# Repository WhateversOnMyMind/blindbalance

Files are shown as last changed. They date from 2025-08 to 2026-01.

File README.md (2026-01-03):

<<<<<<< HEAD
# Objective
Build a device that uses 2 MPU6050 sensors on each elbow to track arm swings (count and distance) to give feedback to user on how to improve arm swing balance and ultimately better posture
=======
>>>>>>> 9a92b26fbc7dfd73c1ad28d76f8ad0d9f775afb2
# Introduction
Hi, this is my project where I try to make a device that tracks your movement with information from a mix of accelerometers and gyroscopes (linear acceleration and radial acceleration) to track arm swings. 

So, why did I start this project?

Let's start from the beginning.
I do this activity at Namsan Mountain where I run with visually impaired runners with a running tether. 

running tether

It keeps the visually impaired runner parallel to the volunteer (me) and lets me pull the runner in case of any obstacles / people. 
Most tethers (all tethers I've seen) are inelastic, thus the blind runners naturally doesn't swing the arm that's tied.
It would be fine if the blind runners switched their tether arm every run, but most runners just make it a habit of using the tether on the same arm always.
Keep running with this habit can become a cause for unbalanced posture.
I didn't notice it in my 2 years of running with visually impaired runners.
But my mom did when she took a look at a group photo that was taken at the event.
Thinking about it, I found out that the blind have a higher COG (center of gravity) velocity ([https://doi.org/10.1002/brb3.1436](https://doi.org/10.1002/brb3.1436)), and thus were more susceptible to bad posture.
This started my journey to find a device to give feedback to blind runners to promote balanced posture through equalizing left and right arm swings (both count and distance).

# 8/4

 - Arduino Basics

→ Learned Digital Inputs
```
    // constants won't change. They're used here to set pin numbers:
    const int buttonPin = 2;     // the number of the pushbutton pin
    const int ledPin =  13;      // the number of the LED pin
    
    // variables will change:
    int buttonState = 0;         // variable for reading the pushbutton status
    
    void setup() {
      // initialize the LED pin as an output:
      pinMode(ledPin, OUTPUT);
      // initialize the pushbutton pin as an input:
      pinMode(buttonPin, INPUT);
    }
    
    void loop() {
      // read the state of the pushbutton value:
      buttonState = digitalRead(buttonPin);
    
      // check if the pushbutton is pressed. If it is, the buttonState is HIGH:
      if (buttonState == HIGH) {
        // turn LED on:
        digitalWrite(ledPin, HIGH);
      } else {
        // turn LED off:
        digitalWrite(ledPin, LOW);
      }
    }
```
→ Learned Analog Inputs and Libraries (And also some debugging & syntax)

Debugging
```
void setup() {
  // initialize serial communication at 9600 bits per second:
  Serial.begin(9600);
}

// the loop routine runs over and over again forever:
void loop() {
  // read the input on analog pin 0:
  int sensorValue = analogRead(A0);
  // print out the value you read:
  Serial.println(sensorValue);
  delay(1);        // delay in between reads for stability
}
```
Analog Inputs + rgb lights
```
#include <Adafruit_NeoPixel.h>
#ifdef __AVR__
 #include <avr/power.h> // Required for 16 MHz Adafruit Trinket
#endif
#define PIN 13
#define NUMPIXELS 3
Adafruit_NeoPixel pixels(NUMPIXELS, PIN, NEO_GRB + NEO_KHZ800);
#define DELAYVAL 500
void color(uint16_t pixelIndex, uint8_t red, uint8_t green, uint8_t blue) {
  pixels.setPixelColor(pixelIndex, pixels.Color(red, green, blue));
}
void setup() {
#if defined(__AVR_ATtiny85__) && (F_CPU == 16000000)
  clock_prescale_set(clock_div_1);
#endif
  pixels.begin();
 pinMode(A0, INPUT);
}

void loop() {
  int raw = analogRead(A0);
  int scrollValue = map(raw, 0, 1023, 0, 255);
  color(0, scrollValue, 0, 0);
  color(1, 0, scrollValue, 0);
  color(2, 0, 0, scrollValue);
  pixels.show();
}
```

 - Sketchup Pro Basics
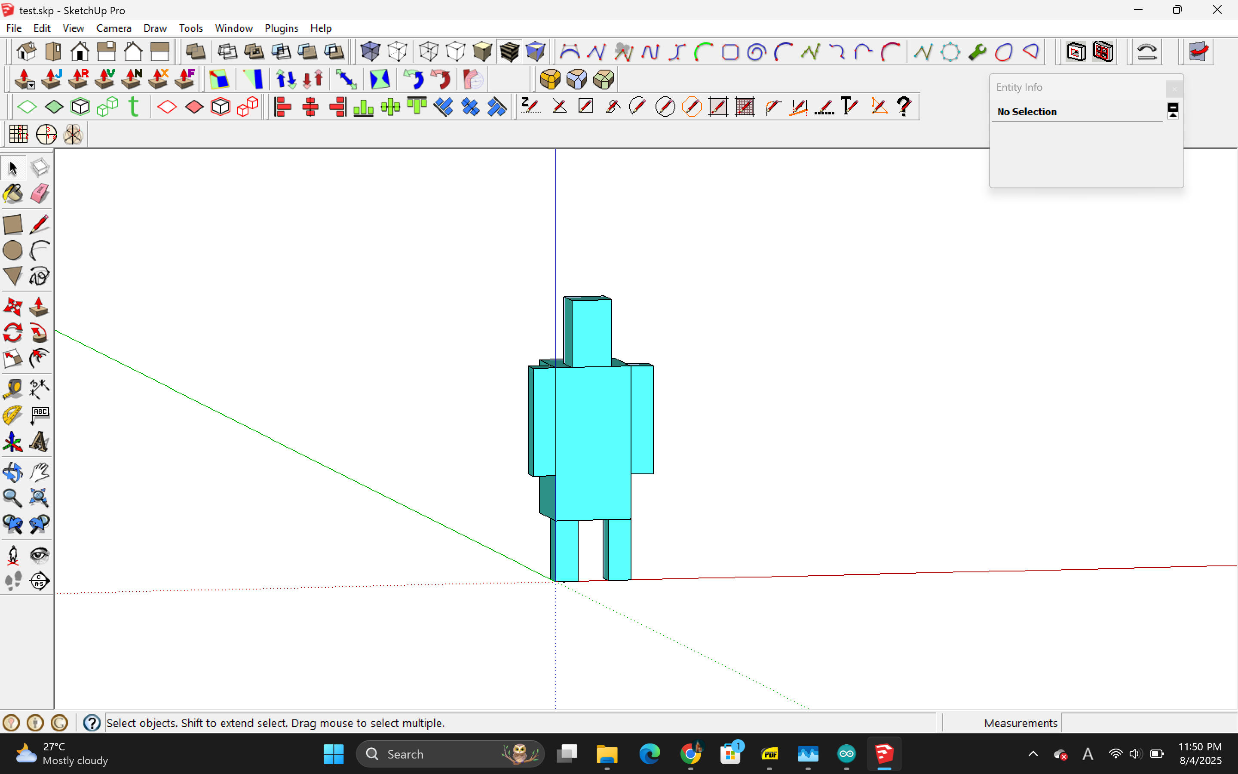
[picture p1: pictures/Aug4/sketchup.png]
Just basic stuff. Can 3-dimensionally print it!!
 

# 8/5
- Arduino coding

Simple double integration model to track motion (print distance every 200ms)
```
#include <Adafruit_MPU6050.h>
#include <Adafruit_Sensor.h>
#include <Wire.h>

Adafruit_MPU6050 mpu;

// ---- calibration storage ----
float axBias = 0, ayBias = 0, azBias = 0;

// ---- state variables ----
float vx = 0, vy = 0, vz = 0;   // velocity (m/s)
float px = 0, py = 0, pz = 0;   // position (m)
unsigned long lastMicros = 0;

void setup() {
  Serial.begin(115200);
  Wire.begin(21, 22);           // LOLIN-D32 default I²C
  if (!mpu.begin()) {
    Serial.println("MPU6050 not found!"); while (1) delay(10);
  }
  mpu.setAccelerometerRange(MPU6050_RANGE_8_G);
  mpu.setFilterBandwidth(MPU6050_BAND_21_HZ);

  Serial.println("\n*** Keep the board STILL for 2 s — calibrating… ***");
  const int N = 400;            // 2 s at 200 Hz
  sensors_event_t a, g, t;
  for (int i = 0; i < N; ++i) {
    mpu.getEvent(&a, &g, &t);
    axBias += a.acceleration.x;
    ayBias += a.acceleration.y;
    azBias += a.acceleration.z - 9.80665;  // remove gravity on Z
    delay(5);
  }
  axBias /= N; ayBias /= N; azBias /= N;
  Serial.println("Calibration done.\n");

  lastMicros = micros();
}

void loop() {
  // -------- time step --------
  unsigned long now = micros();
  float dt = (now - lastMicros) * 1e-6;   // s
  lastMicros = now;

  // -------- read accel --------
  sensors_event_t a, g, t;
  mpu.getEvent(&a, &g, &t);
  float ax = a.acceleration.x - axBias;
  float ay = a.acceleration.y - ayBias;
  float az = a.acceleration.z - azBias;

  // -------- integrate --------
  vx += ax * dt;
  vy += ay * dt;
  vz += az * dt;

  px += vx * dt;
  py += vy * dt;
  pz += vz * dt;

  // -------- print every 200 ms --------
  static unsigned long lastPrint = 0;
  if (millis() - lastPrint >= 200) {
    lastPrint = millis();
    Serial.print("ΔPos X: "); Serial.print(px, 4);
    Serial.print("  Y: ");    Serial.print(py, 4);
    Serial.print("  Z: ");    Serial.print(pz, 4);
    Serial.println("  (m)");
  }
}
```
This time a different approach:
Counts arm swing count by using IMU sensors (MPU6050)
Also has an automatic 2-second gyro sensor calibration period
```
#include <Adafruit_MPU6050.h>
#include <Adafruit_Sensor.h>
#include <Wire.h>

#define SDA_PIN          21
#define SCL_PIN          22
#define SAMPLE_RATE_HZ   250          // loop target ≈ 4 ms
#define GYRO_THRESH      1.2f         // rad/s   (swing detected when |ωz| crosses this)
#define RADIUS_DEFAULT   0.30f        // m       (fore-arm length – user adjustable)
#define CALIB_TIME_MS    2000         // how long to average gyro bias

Adafruit_MPU6050 mpu;

/* ------------------------ runtime state ------------------------ */
float gzBias = 0.0f;                  // gyro Z bias (rad/s)
float radius = RADIUS_DEFAULT;        // swing radius (m)

float angleZ = 0.0f;                  // integrated θ (rad) – continuous
bool  inSwing = false;                // currently inside a swing?
int   dir      = 0;                   // +1 forward, -1 backward
float swingStartAngle = 0.0f;         // θ at swing start
uint32_t swingCount = 0;

uint64_t lastMicros = 0;

/* ----------------------------- helpers ----------------------------- */
void calibrateGyro()
{
  Serial.println(F("\n*** Keep sensor STILL – calibrating gyro (2 s)… ***"));
  delay(500);
  const uint32_t t0 = millis();
  uint32_t samples = 0;
  float sum = 0.0f;
  sensors_event_t a, g, t;
  while (millis() - t0 < CALIB_TIME_MS) {
    mpu.getEvent(&a, &g, &t);
    sum += g.gyro.z;
    ++samples;
    delay(4);
  }
  gzBias = sum / samples;
  Serial.print(F("Gyro Z bias = "));
  Serial.print(gzBias, 6);
  Serial.println(F(" rad/s"));
  angleZ = 0; inSwing = false; dir = 0;
}

void processSerial()
{
  if (!Serial.available()) return;
  char c = Serial.read();
  if (c == 'r')            calibrateGyro();               // recalibrate bias
  else if (c == 'd') {                                   // set new radius
    float newR = Serial.parseFloat();
    if (newR > 0.05 && newR < 1.0) {
      radius = newR;
      Serial.print(F("Swing radius set to "));
      Serial.print(radius * 100.0f, 1);
      Serial.println(F(" cm"));
    }
  }
}

/* ----------------------------- setup ----------------------------- */
void setup()
{
  Serial.begin(115200);
  Wire.begin(SDA_PIN, SCL_PIN);
  if (!mpu.begin()) { Serial.println(F("MPU6050 not found!")); while (1) delay(10); }

  mpu.setGyroRange(MPU6050_RANGE_500_DEG);      //  ±500 °/s  ≈ 8.73 rad/s
  mpu.setFilterBandwidth(MPU6050_BAND_21_HZ);   //  basic LPF

  calibrateGyro();
  lastMicros = micros();

  Serial.println(F("\nSend ‘r’ to recalibrate bias, ‘d <value>’ to set radius in metres\n"));
}

/* ----------------------------- loop ----------------------------- */
void loop()
{
  /* ----- timing ----- */
  uint64_t now = micros();
  float dt = (now - lastMicros) * 1e-6f;
  lastMicros = now;

  /* ----- read IMU ----- */
  sensors_event_t a, g, t;
  mpu.getEvent(&a, &g, &t);
  float wz = g.gyro.z - gzBias;        // rad/s  (Z-axis angular velocity)

  /* ----- integrate θz ----- */
  angleZ += wz * dt;                   // rad (unbounded)

  /* ----- swing detection FSM ----- */
  if (!inSwing) {
    /* detect start: |ω| crosses threshold */
    if (fabsf(wz) > GYRO_THRESH) {
      inSwing           = true;
      dir               = (wz > 0) ? 1 : -1;
      swingStartAngle   = angleZ;
    }
  }
  else {
    /* detect end: sign reversal AND exceeded threshold in opposite dir */
    if ((dir ==  1 && wz < -GYRO_THRESH) ||
        (dir == -1 && wz >  GYRO_THRESH)) {
      float swingEndAngle = angleZ;
      float deltaTheta    = swingEndAngle - swingStartAngle;   // rad (can be ±)
      float arcLen        = fabsf(deltaTheta) * radius;        // m

      ++swingCount;
      Serial.print("Swing #");  Serial.print(swingCount);
      Serial.print(" │ Angle: "); Serial.print(fabsf(deltaTheta) * 57.29578f, 1); Serial.print(" deg");
      Serial.print(" │ Length: "); Serial.print(arcLen * 100.0f, 1); Serial.println(" cm");

      /* ready for next swing */
      inSwing = false;
    }
  }

  processSerial();
  delayMicroseconds(1000000 / SAMPLE_RATE_HZ - 200);   // crude pacing
}
```
Tried some other concepts like counting when angular acceleration turned negative or when it reached zero, but those attempts didn't work as well since human movements are a bit unpredictable → counted mid-swing

Eventually stuck with the above code although with more polishing and adjustments
I didn't really why it still gave me false counts (swings), turns out I had to use the y-axis instead of the z-axis.
Also, I separated the swing thresholds for forward and backward motion and made both lower than the original thresholds since, well, you don't really drastically swing your arms when you're jogging right?
```
#include <Adafruit_MPU6050.h>
#include <Adafruit_Sensor.h>
#include <Wire.h>

/* ── pins ── */
#define SDA_PIN              21
#define SCL_PIN              22

/* ── sampling & calibration ── */
#define SAMPLE_RATE_HZ       250        // ≈4 ms loop
#define CALIB_TIME_MS        2000       // 2 s gyro-bias average

/* ── swing thresholds (provided) ── */
#define GYRO_THRESH_FWD      0.4f       // rad/s  forward swing must exceed
#define GYRO_THRESH_BACK     0.2f       // rad/s  backward swing must exceed
#define MIN_DELTA_THETA      0.12f      // rad ≈ 7°  ignore tiny jitters

/* ── geometry ── */
#define RADIUS_DEFAULT       0.30f      // m  elbow→wrist

/* ── globals ── */
Adafruit_MPU6050 mpu;

float gyBias  = 0.0f;                  // Y-axis bias
float radius  = RADIUS_DEFAULT;

bool  inSwing = false;
int   dir     = 0;                     // +1 = forward, –1 = backward
float angle   = 0.0f;                  // integrated θ about Y (rad)
float startAngle = 0.0f;
uint32_t swingCount = 0;

uint64_t lastMicros = 0;

/* ─────────── helpers ─────────── */
void printSwing(float endAngle)
{
  float dTheta = endAngle - startAngle;
  if (fabsf(dTheta) < MIN_DELTA_THETA) { inSwing = false; return; }  // too small

  ++swingCount;
  float arcLen = fabsf(dTheta) * radius;            // m

  Serial.print(F("Swing #"));  Serial.print(swingCount);
  Serial.print(F(" │ Angle: "));  Serial.print(fabsf(dTheta) * 57.29578f, 1);
  Serial.print(F(" ° │ Length: ")); Serial.print(arcLen * 100.0f, 1);
  Serial.println(F(" cm"));
  inSwing = false;
}

void calibrateGyro()
{
  Serial.println(F("\n*** Keep sensor STILL – calibrating (2 s)… ***"));
  delay(400);
  uint32_t t0 = millis();  float sum = 0;  uint32_t n = 0;
  sensors_event_t a, g, t;
  while (millis() - t0 < CALIB_TIME_MS) {
    mpu.getEvent(&a, &g, &t);
    sum += g.gyro.y;  ++n;  delay(4);
  }
  gyBias = sum / n;

  swingCount = 0; angle = 0; inSwing = false; dir = 0;
  Serial.print(F("Gyro-Y bias = ")); Serial.print(gyBias, 6); Serial.println(F(" rad/s"));
}

void serialMenu()
{
  if (!Serial.available()) return;
  char c = Serial.read();
  if (c == 'r') calibrateGyro();
  else if (c == 'd') {
    float r = Serial.parseFloat();
    if (r > 0.05 && r < 1.0) {
      radius = r;
      Serial.print(F("Radius set to ")); Serial.print(radius * 100.0f, 1);
      Serial.println(F(" cm"));
    }
  }
}

/* ─────────── setup ─────────── */
void setup()
{
  Serial.begin(115200);
  Wire.begin(SDA_PIN, SCL_PIN);

  if (!mpu.begin()) { Serial.println(F("MPU6050 not found!")); while (1) delay(10); }
  mpu.setGyroRange(MPU6050_RANGE_500_DEG);          // ±500 °/s
  mpu.setFilterBandwidth(MPU6050_BAND_21_HZ);

  calibrateGyro();
  lastMicros = micros();

  Serial.println(F("\nCommands:  r = recalibrate  |  d <metres> = set radius\n"));
}

/* ─────────── loop ─────────── */
void loop()
{
  /* Δt */
  uint64_t now = micros();
  float dt = (now - lastMicros) * 1e-6f;
  lastMicros = now;

  /* IMU */
  sensors_event_t a, g, t;  mpu.getEvent(&a, &g, &t);
  float wy = g.gyro.y - gyBias;          // rad/s   USING Y-AXIS ONLY

  /* integrate θ about Y */
  angle += wy * dt;

  /* FSM */
  if (!inSwing)                              // waiting for stroke start
  {
    if (wy >  GYRO_THRESH_FWD)               // forward stroke begins
      { inSwing = true; dir = +1; startAngle = angle; }
    else if (wy < -GYRO_THRESH_BACK)         // backward stroke begins
      { inSwing = true; dir = -1; startAngle = angle; }
  }
  else                                        // inside a stroke
  {
    if (dir == +1 && wy < -GYRO_THRESH_BACK)      // forward finished
        printSwing(angle);
    else if (dir == -1 && wy >  GYRO_THRESH_FWD)  // backward finished
        printSwing(angle);
  }

  serialMenu();
  delayMicroseconds(1000000 / SAMPLE_RATE_HZ - 200);
}
```
- Controller Housing Modeling

Planned to use 30x70mm PCB board (because I'm going to use 2 sensors).
Thus, the model is sized at 94x54x32 (2 mm thickness and without a cover).
Has 3 mm wide holes to put screws to hold the contents.
Has holes for wires too.

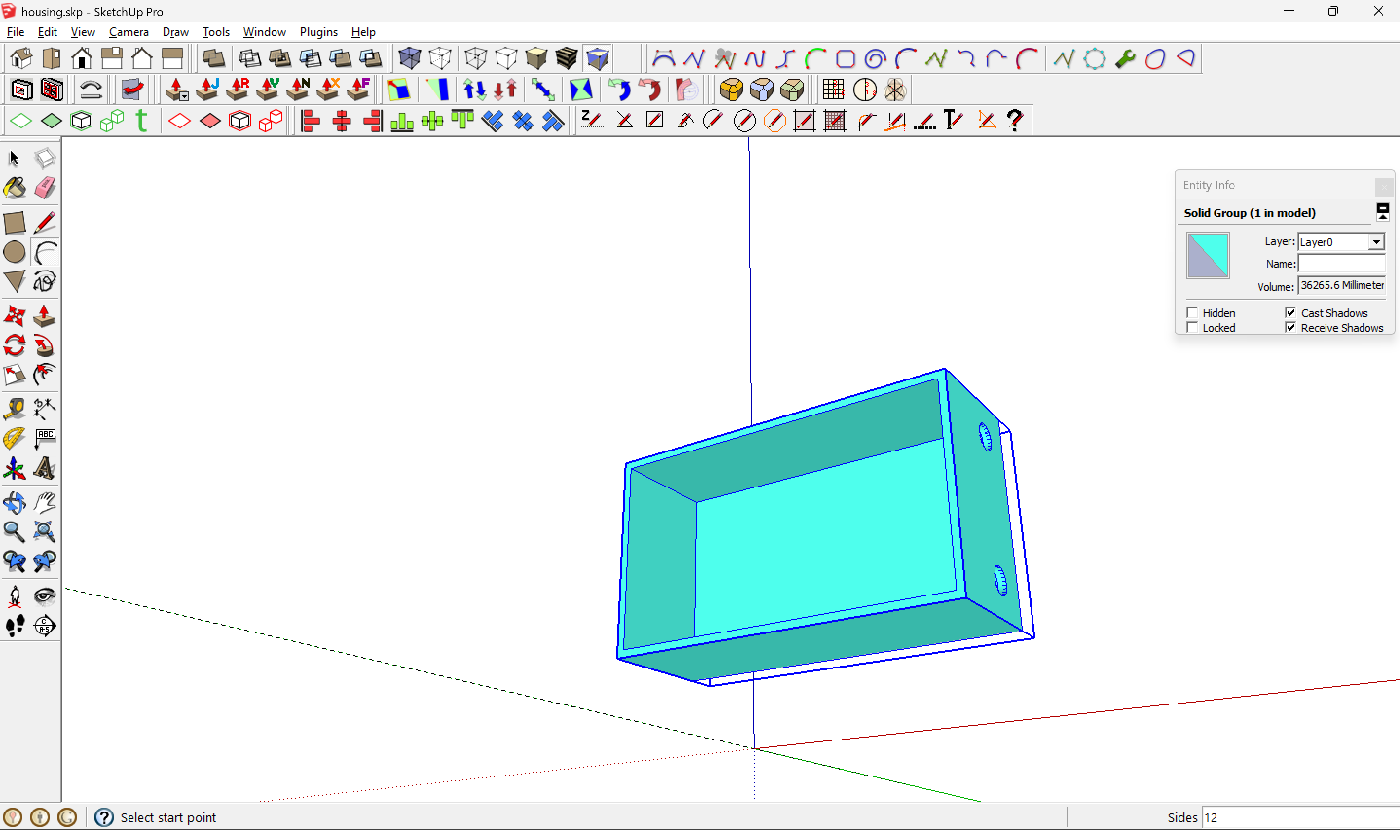
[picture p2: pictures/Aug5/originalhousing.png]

original version ^
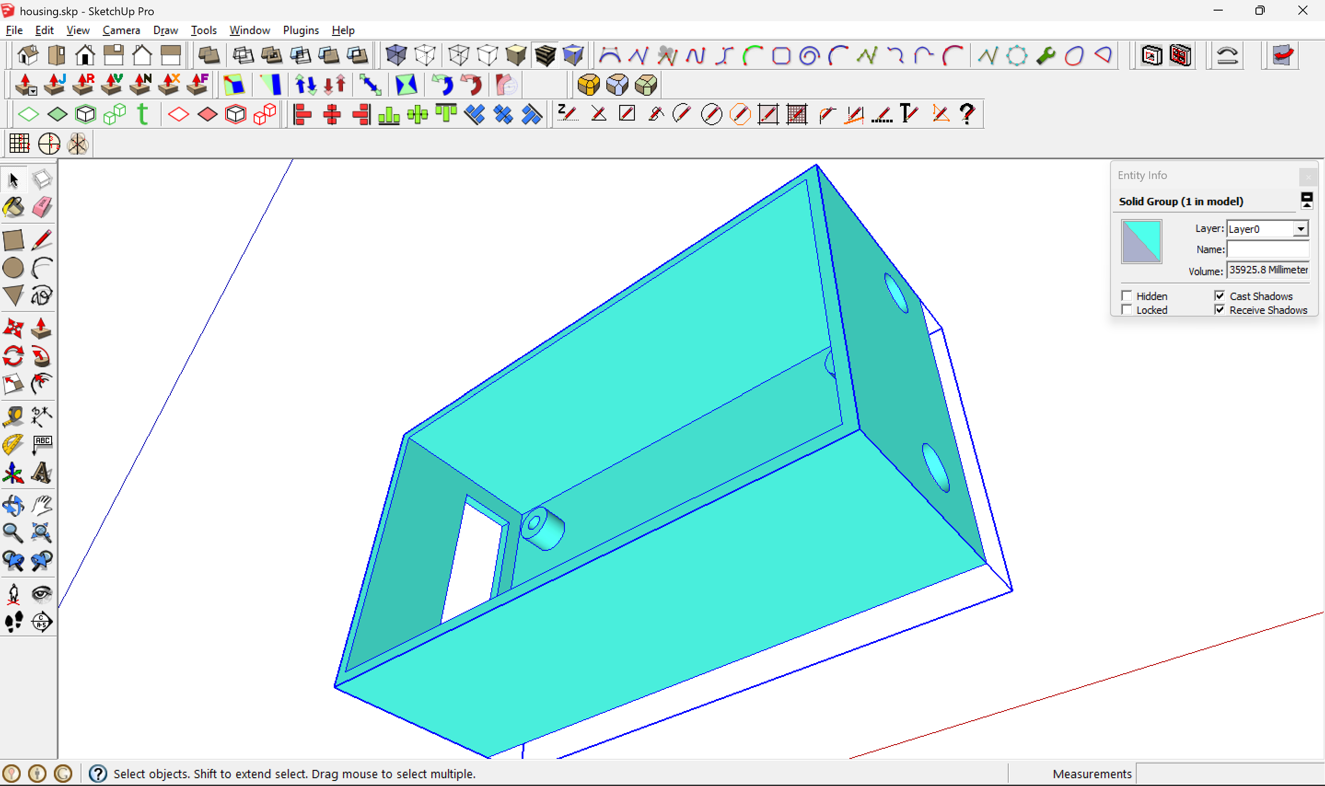
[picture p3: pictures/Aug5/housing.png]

revised version with screw holes ^

the back has a clip made for easy hanging (from a shirt) ^

# 8/6
- Sensor housing

Made a prototype sensor model that could stay on the wristband I bought at *Daiso*. The wristband was supposed to be wound twice so it did fit around my upper elbow.
Probably going to buy a real armband (or an 'elbow band' if that exists) in the future. I just need a replacement for the real thing today (delivery takes a day), so for now, this works.
Measured at 50mm width, it was quite flexible so I put the entry point at 14mm.
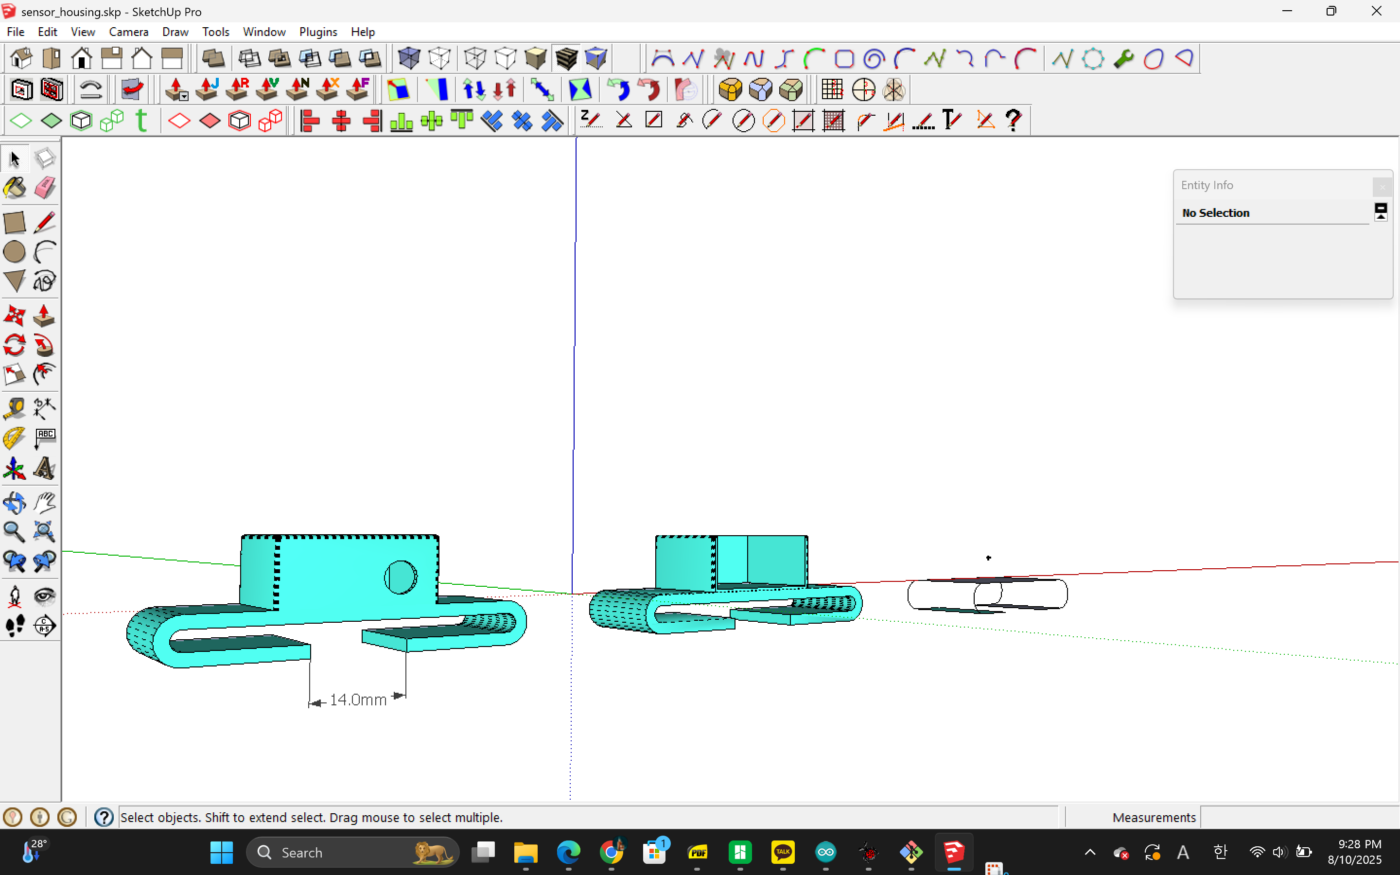
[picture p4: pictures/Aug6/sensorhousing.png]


- Controller Housing Revision
Apparently, The cables didn't go through the holes on the top very well, so I added a square hole on top of the circle so it looks like this: [0] (Forgive me for the not so accurate description)
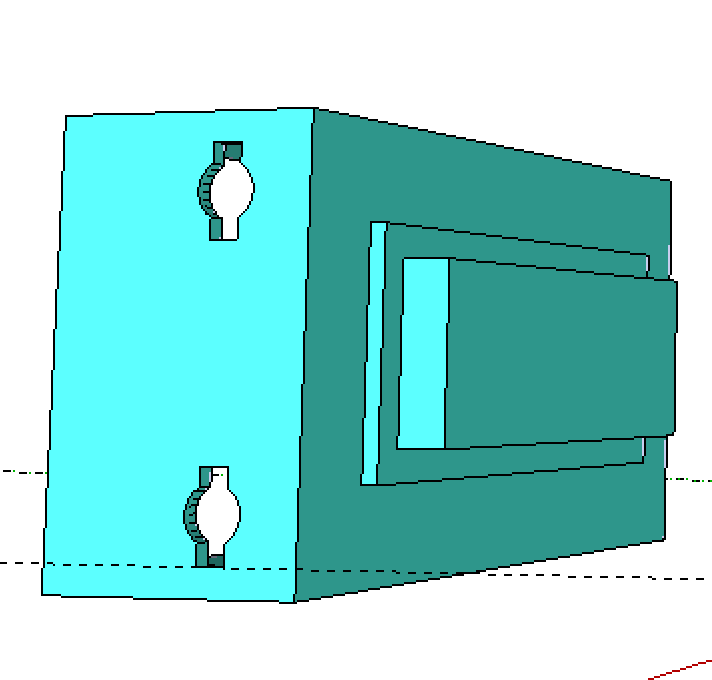
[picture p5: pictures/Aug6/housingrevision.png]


# 8/7
- Need a new casing for the controller
→ 63x27mm was the PCB plate's screw hole rectangle
3D printed it. There were some little inaccuracies, but it still fit.
Will probably widen it by a millimeter next time.
The battery did fit but it did require some force to make it work. There were marks on the battery case when I unscrewed the controller. (Because of the solder tails)
Will also heighten the screw holes by around 3 mm to make the battery fit better.

New code for 2 MPU6050 sensors
```
#include <Adafruit_MPU6050.h>
#include <Adafruit_Sensor.h>
#include <Wire.h>

/* ── pins ── */
#define SDA_PIN              21
#define SCL_PIN              22

/* ── addresses ── */
#define ADDR_LEFT            0x68
#define ADDR_RIGHT           0x69

/* ── sampling & calibration ── */
#define SAMPLE_RATE_HZ       250
#define CALIB_TIME_MS        2000

/* ── thresholds ── */
#define GYRO_THRESH_FWD      0.4f
#define GYRO_THRESH_BACK     0.2f
#define MIN_DELTA_THETA      0.12f

#define RADIUS_DEFAULT       0.30f

Adafruit_MPU6050 mpuLeft;
Adafruit_MPU6050 mpuRight;

struct Arm {
  Adafruit_MPU6050* mpu;
  float bias;
  float radius;
  bool inSwing;
  int dir;
  float angle;
  float startAngle;
  uint32_t swingCount;
  const char* label;
};

Arm left = { &mpuLeft, 0.0f, RADIUS_DEFAULT, false, 0, 0.0f, 0.0f, 0, "L" };
Arm right = { &mpuRight, 0.0f, RADIUS_DEFAULT, false, 0, 0.0f, 0.0f, 0, "R" };

uint64_t lastMicros = 0;

void calibrateGyro(Arm &arm) {
  Serial.print(F("Calibrating ")); Serial.println(arm.label);
  delay(400);
  uint32_t t0 = millis();
  float sum = 0; uint32_t n = 0;
  sensors_event_t a, g, t;
  while (millis() - t0 < CALIB_TIME_MS) {
    arm.mpu->getEvent(&a, &g, &t);
    sum += g.gyro.y; ++n; delay(4);
  }
  arm.bias = sum / n;
  arm.angle = 0; arm.dir = 0; arm.inSwing = false; arm.swingCount = 0;
  Serial.print(arm.label); Serial.print(F(" bias = "));
  Serial.println(arm.bias, 6);
}

void printSwing(Arm &arm, float endAngle) {
  float dTheta = endAngle - arm.startAngle;
  if (fabsf(dTheta) < MIN_DELTA_THETA) { arm.inSwing = false; return; }

  ++arm.swingCount;
  float arcLen = fabsf(dTheta) * arm.radius;
  Serial.print(F("Swing ")); Serial.print(arm.label);
  Serial.print(F(" #")); Serial.print(arm.swingCount);
  Serial.print(F(" │ Angle: ")); Serial.print(fabsf(dTheta) * 57.29578f, 1);
  Serial.print(F(" ° │ Length: ")); Serial.print(arcLen * 100.0f, 1);
  Serial.println(F(" cm"));

  arm.inSwing = false;
}

void updateArm(Arm &arm, float dt) {
  sensors_event_t a, g, t;
  arm.mpu->getEvent(&a, &g, &t);
  float wy = g.gyro.y - arm.bias;
  arm.angle += wy * dt;

  if (!arm.inSwing) {
    if (wy > GYRO_THRESH_FWD) {
      arm.inSwing = true; arm.dir = +1; arm.startAngle = arm.angle;
    }
    else if (wy < -GYRO_THRESH_BACK) {
      arm.inSwing = true; arm.dir = -1; arm.startAngle = arm.angle;
    }
  }
  else {
    if (arm.dir == +1 && wy < -GYRO_THRESH_BACK)
      printSwing(arm, arm.angle);
    else if (arm.dir == -1 && wy > GYRO_THRESH_FWD)
      printSwing(arm, arm.angle);
  }
}

void setup() {
  Serial.begin(115200);
  Wire.begin(SDA_PIN, SCL_PIN);

  if (!mpuLeft.begin(ADDR_LEFT)) {
    Serial.println(F("Left MPU6050 not found!")); while (1) delay(10);
  }
  if (!mpuRight.begin(ADDR_RIGHT)) {
    Serial.println(F("Right MPU6050 not found!")); while (1) delay(10);
  }

  mpuLeft.setGyroRange(MPU6050_RANGE_500_DEG);
  mpuRight.setGyroRange(MPU6050_RANGE_500_DEG);
  mpuLeft.setFilterBandwidth(MPU6050_BAND_21_HZ);
  mpuRight.setFilterBandwidth(MPU6050_BAND_21_HZ);

  calibrateGyro(left);
  calibrateGyro(right);

  lastMicros = micros();
}

void loop() {
  uint64_t now = micros();
  float dt = (now - lastMicros) * 1e-6f;
  lastMicros = now;

  updateArm(left, dt);
  updateArm(right, dt);

  delayMicroseconds(1000000 / SAMPLE_RATE_HZ - 200);
}
```
Didn't work. Not because of the code though.
The MPU6050 can be signalled through 2 addresses: 0x68 and 0x69.
And to give these addresses, 0x68 needs a LOW and 0x69 needs a HIGH signal from the 5V pin. That requires 5 pins in total (4 (original) +1 (5V)) and I only have 4x2 pins made on my PCB board. But the sensor with the address 0x69 needs to get a 5V signal regardless…so I just soldered the ADD pin to the VCC pin.
Seems to be working fine.…for now.

# 8/8
- Feedback feature by vibrations 

I ordered vibration motors but they didn't come today so I tested if the feedback feature would work correctly with serial.

original feedback function (serial)
```
if ((left.swingCount + right.swingCount) == 0) {
    Serial.println("swingCount sum is 0");
    return;
}

if ((left.swingDistanceSum + right.swingDistanceSum) == 0) {
    Serial.println("swingDistanceSum sum is 0");
    return;
}

float countDiff = float(left.swingCount - right.swingCount) /
                  float(left.swingCount + right.swingCount);

float distanceDiff = (left.swingDistanceSum - right.swingDistanceSum) /
                     (left.swingDistanceSum + right.swingDistanceSum);

float diff = (countDiff + distanceDiff) / 2.0f; // 0.0 → 1.0

if (diff < 0.11f && diff > -0.11f) {
    Serial.println("good");
    return;
}

if (diff > 0)
    Serial.println("Move your right arm more");
else
    Serial.println("Move your left arm more");
```

- New controller housing
Like I mentioned, I needed to make the gap between screws bigger (1mm) and make the screw holes 3mm higher (so 9mm height in total)
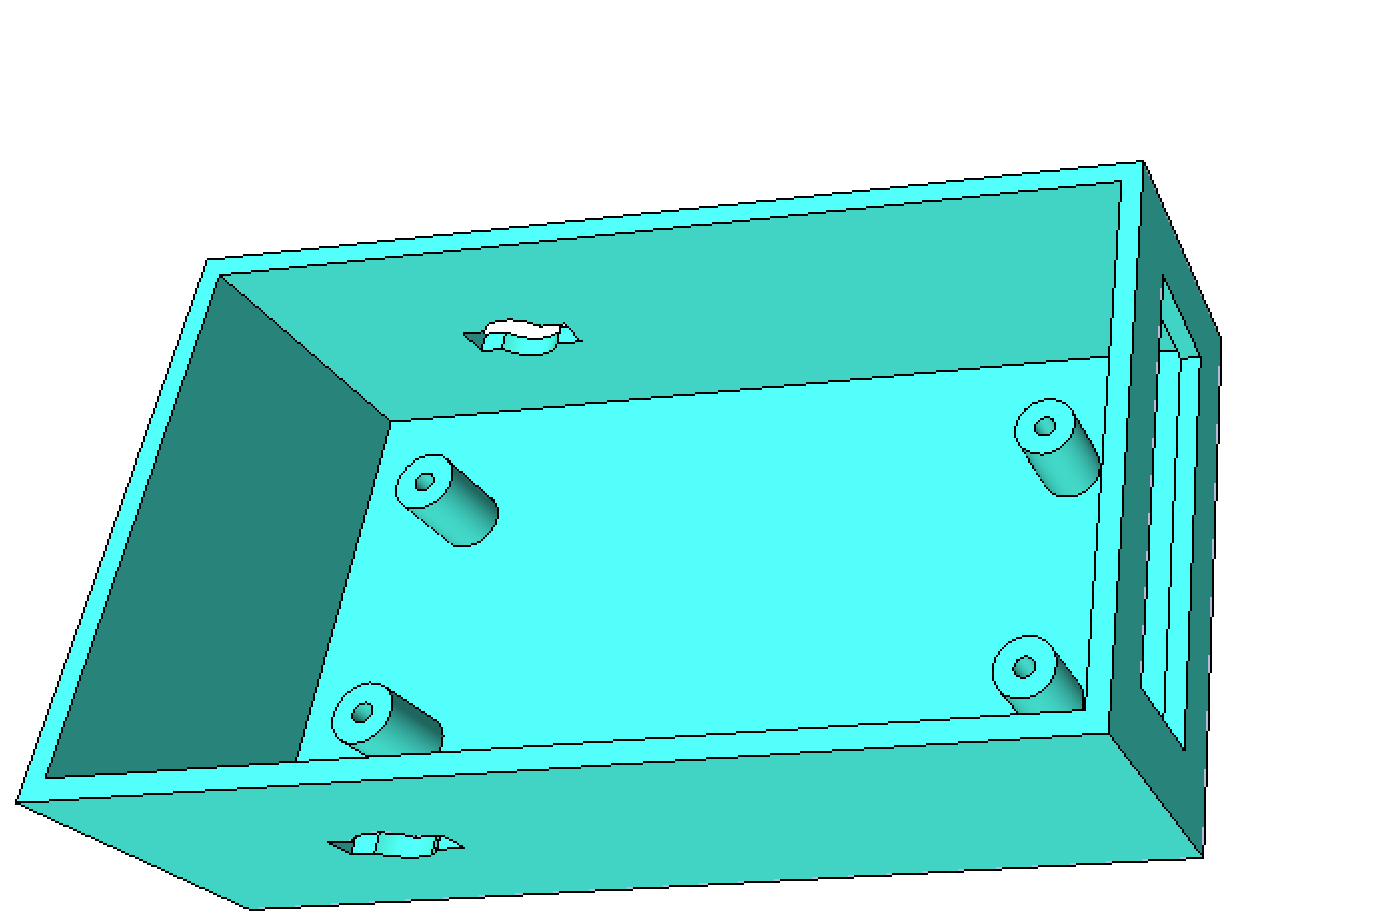
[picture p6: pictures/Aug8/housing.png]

I also noticed that the cable placement was kind of awkward in the earlier model so I flipped the top and bottom switch holes and then moved the holes for the cable that goes to the sensor to the left and right since, well, the sensors are on the left and right.

- New sensor housing
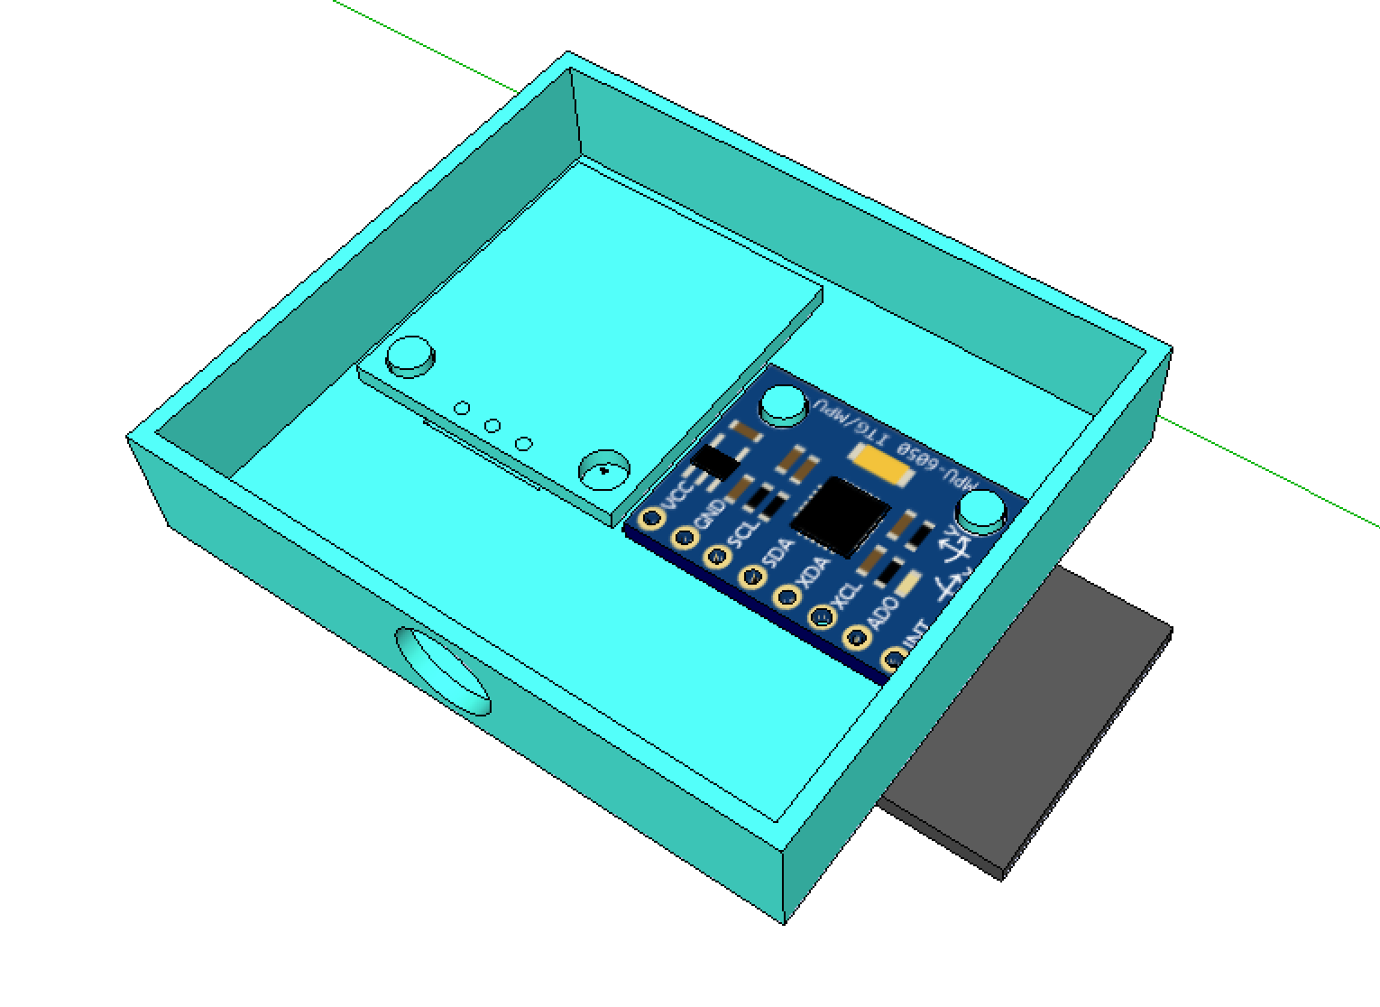
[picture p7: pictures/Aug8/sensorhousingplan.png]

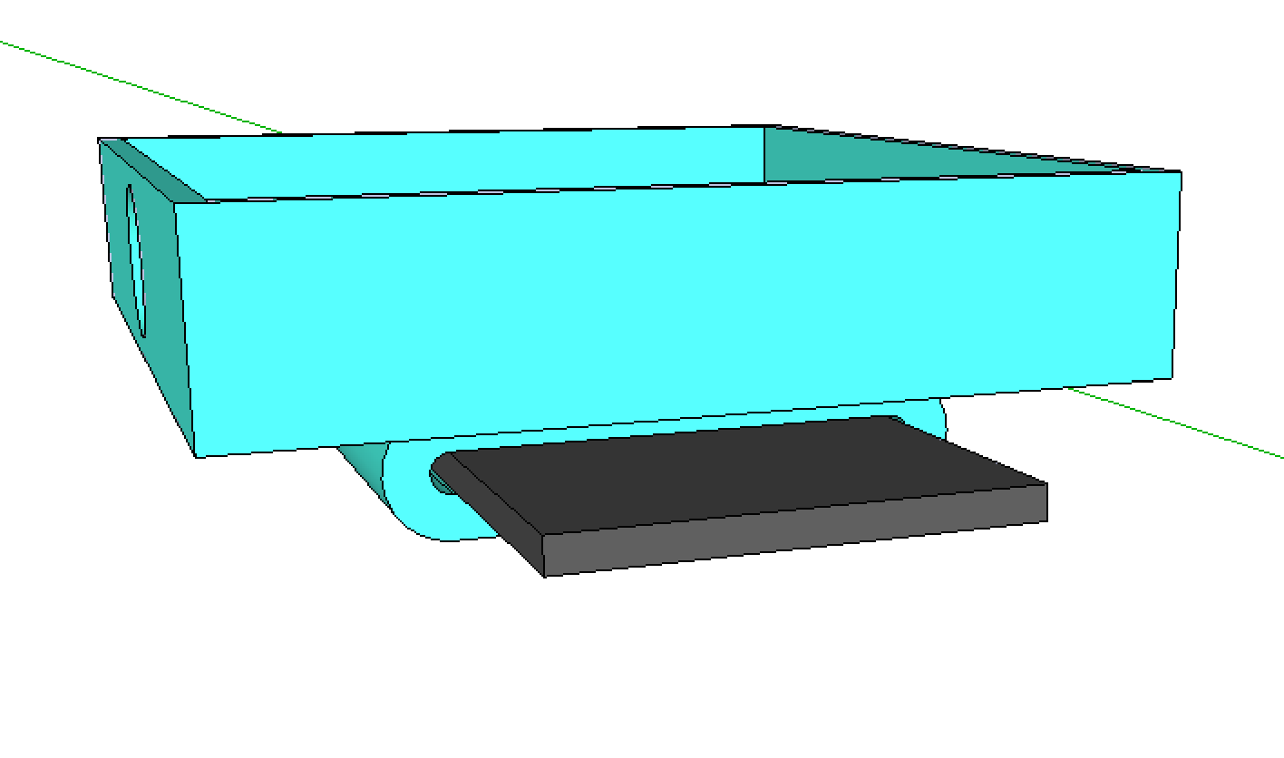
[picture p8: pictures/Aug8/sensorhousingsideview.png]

Changed a LOT of things here.
   1. Changed the clip to be in the perpendicular direction of the main body where the sensor goes
   2. Because the arm band finally came, the clip is a lot smaller
	   
   3. Widened the main body to accommodate the vibration motor. (Not here yet but will be in a few days)
  4. The clip looks and feels more ergonomic (?), it's more curvy and round.
  5. And the hole for the wire is at the center now.

Also, there was a problem with the previous housing where sometimes the sensors disconnected or malfunctioned with no apparent reason, and I thought it was because the sensor housing fit too tight and was messing around with the cables. The new (final) version made it a much looser fit, but still gave me errors.
It seems that soldering doesn't work very well in moving parts (I even wrapped heat shrinking tubes to secure the connection). Will probably find another way one way or another.

# 8/16
Finally, the wires came.
Soldering weren't that great for hardware that moved.
Thus, another solution I found was Dupont connectors to just clip them into place.
It took a while, but it did result in a much smoother user experience.

Another issue I had was that the sensor housing didn't have enough space for the *Duponted* wires. So I just stretched the sensor housing by 5mms. That got rid of the issue, but now it's still really hard to disassemble hardware.

However, what matters is that it now works.

Here is the full code with all the tricks (including motor vibrational feedback)
```
/****************************************************************************************
  Jog Arm-Swing Counter – Y-axis + 60-second stats   (ESP32 LOLIN-D32  +  MPU6050)
****************************************************************************************/
#include <Adafruit_MPU6050.h>
#include <Adafruit_Sensor.h>
#include <Wire.h>

/* ── pins ── */
#define SDA_PIN              21
#define SCL_PIN              22

/* ── sampling & calibration ── */
#define SAMPLE_RATE_HZ       250
#define CALIB_TIME_MS        2000

/* ── swing thresholds ── */
#define GYRO_THRESH_FWD      0.4f       // rad/s
#define GYRO_THRESH_BACK     0.2f
#define MIN_DELTA_THETA      0.12f      // rad ≈7°

/* ── geometry ── */
#define RADIUS_DEFAULT       0.30f      // m

/* ── globals ── */
Adafruit_MPU6050 mpu;
float gyBias = 0.0f;
float radius = RADIUS_DEFAULT;

bool  inSwing = false;
int   dir = 0;
float angle = 0.0f, startAngle = 0.0f;
uint32_t swingCount = 0;
uint64_t lastMicros = 0;

/* 60-s window */
uint32_t windowStartMs = 0;
uint32_t minuteSwingCount = 0;
float    minuteDistance   = 0.0f;      // m

/* ─────────── helpers ─────────── */
void printSwing(float endAngle)
{
  float dTheta = endAngle - startAngle;
  if (fabsf(dTheta) < MIN_DELTA_THETA) { inSwing = false; return; }

  ++swingCount;
  float arcLen = fabsf(dTheta) * radius;     // m

  /* add to 60-s stats */
  ++minuteSwingCount;
  minuteDistance += arcLen;

  Serial.print(F("Swing #"));  Serial.print(swingCount);
  Serial.print(F(" │ Angle: "));  Serial.print(fabsf(dTheta)*57.29578f,1);
  Serial.print(F(" ° │ Length: ")); Serial.print(arcLen*100.0f,1);
  Serial.println(F(" cm"));
  inSwing = false;
}

void maybePrintMinuteStats()
{
  uint32_t now = millis();
  if (now - windowStartMs >= 60000UL) {           // 60 s elapsed
    Serial.print(F("[1-min] Swings: "));
    Serial.print(minuteSwingCount);
    Serial.print(F(" │ Distance: "));
    Serial.print(minuteDistance*100.0f,1);        // cm
    Serial.println(F(" cm"));

    /* reset window */
    windowStartMs    = now;
    minuteSwingCount = 0;
    minuteDistance   = 0.0f;
  }
}

void calibrateGyro()
{
  Serial.println(F("\n*** Keep sensor STILL – calibrating (2 s)… ***"));
  delay(400);
  uint32_t t0 = millis();  float sum = 0;  uint32_t n = 0;
  sensors_event_t a,g,t;
  while (millis()-t0 < CALIB_TIME_MS){ mpu.getEvent(&a,&g,&t); sum += g.gyro.y; ++n; delay(4);}
  gyBias = sum / n;

  swingCount = 0; angle = 0; inSwing = false; dir = 0;
  windowStartMs = millis(); minuteSwingCount = 0; minuteDistance = 0;
  Serial.print(F("Gyro-Y bias = ")); Serial.print(gyBias,6); Serial.println(F(" rad/s"));
}

void serialMenu()
{
  if (!Serial.available()) return;
  char c = Serial.read();
  if (c=='r') calibrateGyro();
  else if (c=='d'){
    float r=Serial.parseFloat();
    if(r>0.05&&r<1.0){radius=r;Serial.print(F("Radius set to "));
      Serial.print(radius*100.0f,1);Serial.println(F(" cm"));}}
}

/* ─────────── setup ─────────── */
void setup()
{
  Serial.begin(115200);
  Wire.begin(SDA_PIN, SCL_PIN);

  if(!mpu.begin()){Serial.println(F("MPU6050 not found!"));while(1)delay(10);}
  mpu.setGyroRange(MPU6050_RANGE_500_DEG);
  mpu.setFilterBandwidth(MPU6050_BAND_21_HZ);

  calibrateGyro();
  lastMicros = micros();

  Serial.println(F("\nCommands:  r = recalibrate  |  d <metres> = set radius\n"));
}

/* ─────────── loop ─────────── */
void loop()
{
  /* Δt */
  uint64_t now = micros();
  float dt = (now - lastMicros)*1e-6f;
  lastMicros = now;

  /* IMU */
  sensors_event_t a,g,t;  mpu.getEvent(&a,&g,&t);
  float wy = g.gyro.y - gyBias;

  /* integrate θ */
  angle += wy * dt;

  /* FSM */
  if(!inSwing)
  {
    if (wy >  GYRO_THRESH_FWD)   { inSwing=true; dir=+1; startAngle=angle; }
    else if (wy < -GYRO_THRESH_BACK){ inSwing=true; dir=-1; startAngle=angle;}
  }
  else
  {
    if (dir==+1 && wy < -GYRO_THRESH_BACK) printSwing(angle);
    else if (dir==-1 && wy >  GYRO_THRESH_FWD) printSwing(angle);
  }

  maybePrintMinuteStats();
  serialMenu();
  delayMicroseconds(1000000/SAMPLE_RATE_HZ - 200);
}
```
This also outputs data to google sheets so I also made a small website to analyze the data.
[Link](blindrunning.com/data)

# 12/31 (Happy New Years) (The Big 26 Now)

It's been quite some time since I journaled my progress but nevertheless I didn't stop upgrading my device.
There was this huge problem where the single Li-ion battery didn't have enough power to maintain both the IMUs, both the vibration motors, and the microcontroller at the same time. I fixed it with two Li-ion batteries, one powering the IMUs and the MCU and the other powering the vibration motor.

Still, I kinda felt like it was inconvient for the user to charge two seperate batteries simultaenously so I thought about a way to fix this issue.
Making the device not connect back to a single MCU and making just two cases to support the MCU, vibration motor, and the IMU looked like a good idea.

So i started wiring but I did cause a short accidently and blew the battery and the charging module and waste a hell lot of time but it was fixed.



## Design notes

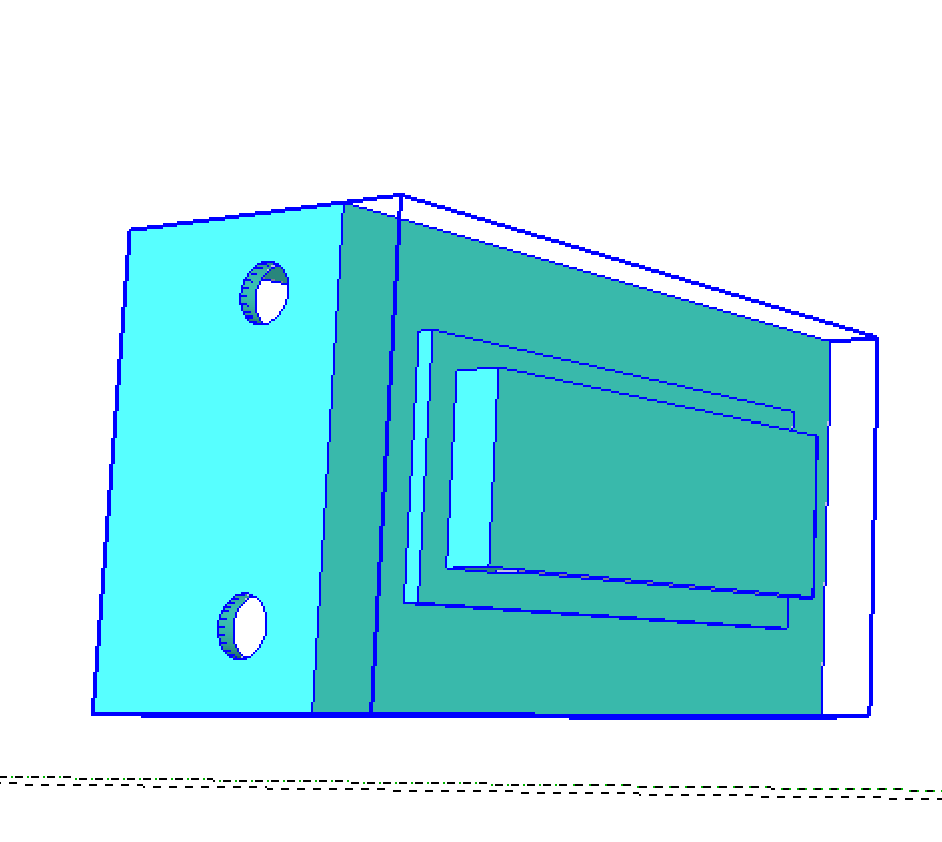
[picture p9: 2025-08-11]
pictures/Aug5/back.pmg.png

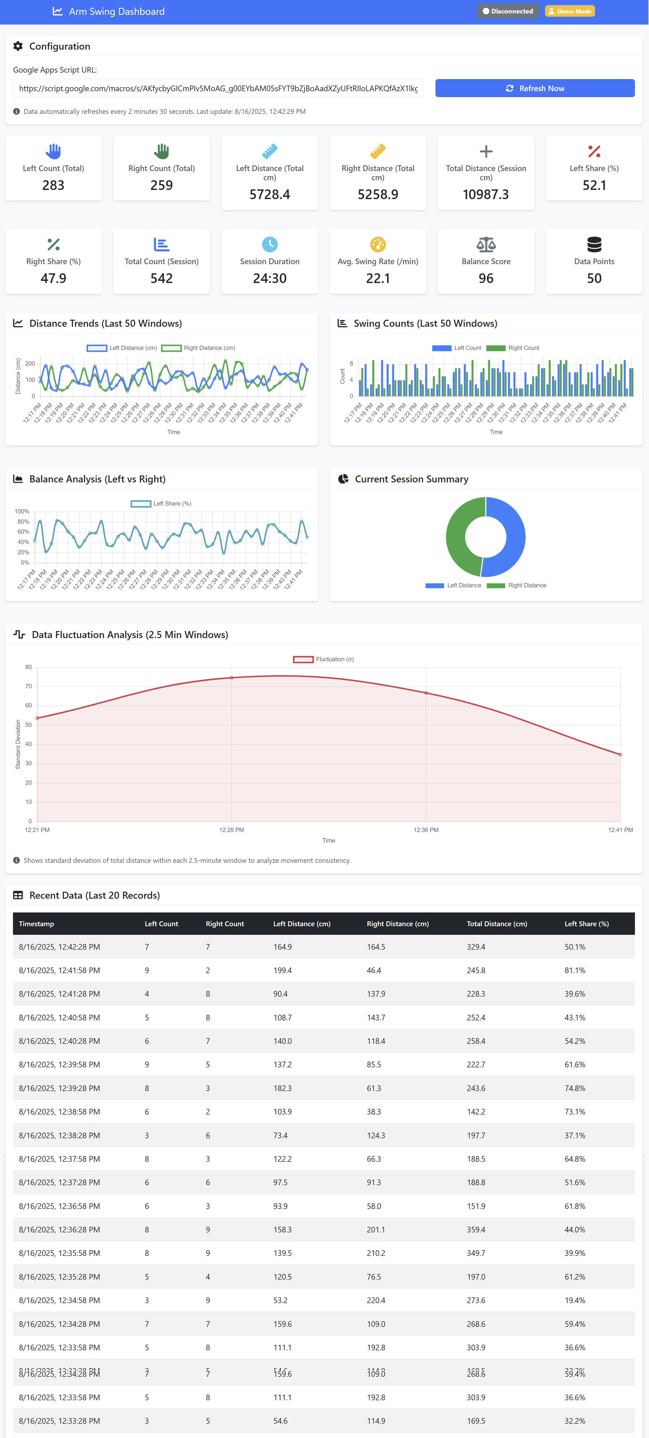
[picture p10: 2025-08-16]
pictures/website/screenshot.png

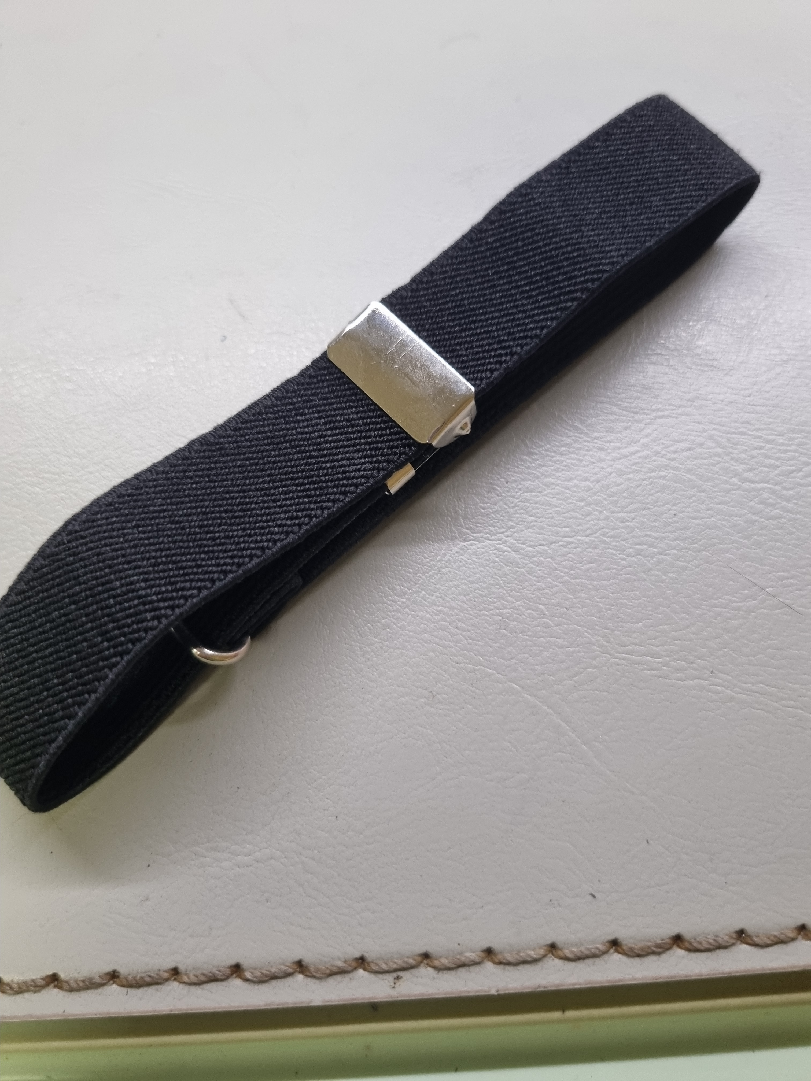
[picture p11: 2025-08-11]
pictures/Aug8/armband.jpg

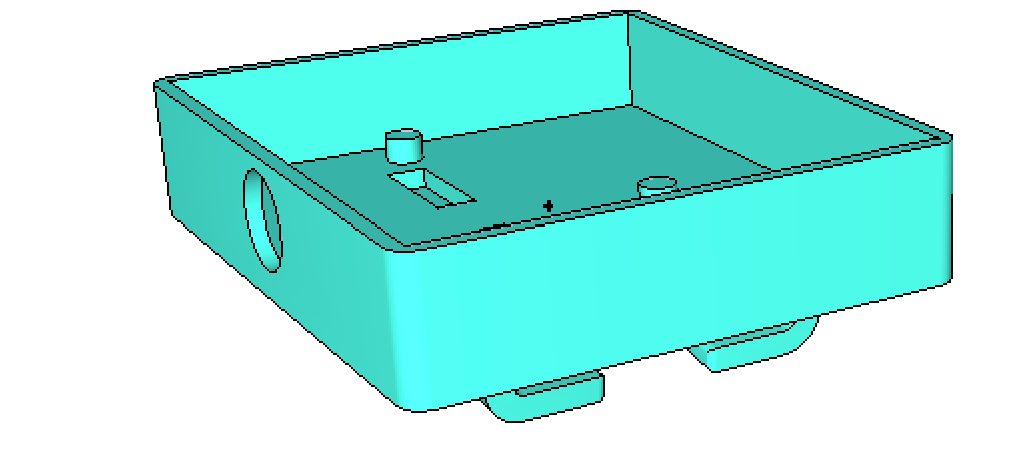
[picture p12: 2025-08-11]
pictures/Aug8/finalsensorhousing.png

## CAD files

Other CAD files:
tether/106.skp

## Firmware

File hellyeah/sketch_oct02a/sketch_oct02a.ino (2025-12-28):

#include <Adafruit_MPU6050.h>
#include <Adafruit_Sensor.h>
#include <Wire.h>
#include <WiFi.h>
#include <HTTPClient.h>
#include <vector>
#include <algorithm>

/* ── WiFi ── */
const char* ssid = "GalaxyS23";
const char* password = "12345678";
const char* scriptURL = "https://script.google.com/macros/s/AKfycbzBvJKEtq9sOr6JkIPRjNUf_4xROrjfYzzAtlElzlUsUg69tv45QoupNosSsXKZQs7l/exec";

/* ── pins ── */
#define SDA_PIN 21
#define SCL_PIN 22
#define PIN_VIBE_LEFT 17
#define PIN_VIBE_RIGHT 16

/* ── addresses ── */
#define ADDR_LEFT 0x69
#define ADDR_RIGHT 0x68

/* ── sampling & calibration ── */
#define SAMPLE_RATE_HZ 250
#define CALIB_TIME_MS 2000

/* ── thresholds (default, updated by priming) ── */
float GYRO_THRESH_FWD = 0.4f;
float GYRO_THRESH_BACK = 0.4f;
#define MIN_DELTA_THETA 0.2f
#define RADIUS_DEFAULT 0.30f
float ACCEL_MAG_THRESH_DELTA = 2.0f;

/* ── swing robustness ── */
#define SWING_MAX_MS 1200
#define WY_IDLE 0.12f
#define END_ZERO_CROSS_MS 180
#define BIAS_ADAPT_ALPHA 0.0008f

Adafruit_MPU6050 mpuLeft;
Adafruit_MPU6050 mpuRight;

struct Arm {
  Adafruit_MPU6050* mpu;
  float bias;
  float radius;
  bool inSwing;
  int dir;
  float angle;
  float startAngle;
  uint32_t swingCount;
  float swingDistanceSum;
  const char* label;
  uint32_t lastSwingTime;
  uint32_t swingStartMs;
};

Arm left  = { &mpuLeft, 0.0f, RADIUS_DEFAULT, false, 0, 0.0f, 0.0f, 0, 0.0f, "L", 0, 0 };
Arm right = { &mpuRight, 0.0f, RADIUS_DEFAULT, false, 0, 0.0f, 0.0f, 0, 0.0f, "R", 0, 0 };

uint64_t lastMicros = 0;
unsigned long lastSendTime = 0;

/* ── Serial-safe print macros ── */
#define PRINTLN(x) if(Serial) Serial.println(x)
#define PRINT(x) if(Serial) Serial.print(x)

/* ── Calibration ── */
void calibrateGyro(Arm &arm) {
  PRINTLN("Calibrating "+String(arm.label));
  delay(400);
  uint32_t t0 = millis();
  float sum = 0; uint32_t n = 0;
  sensors_event_t a, g, t;
  while (millis() - t0 < CALIB_TIME_MS) {
    arm.mpu->getEvent(&a, &g, &t);
    sum += g.gyro.y; ++n; delay(4);
  }
  arm.bias = sum / n;
  arm.angle = 0; arm.dir = 0; arm.inSwing = false; arm.swingCount = 0;
  PRINT("Bias "+String(arm.label)+" = "); PRINTLN(arm.bias);
}

/* ── Swing print ── */
void printSwing(Arm &arm, float endAngle) {
  uint32_t now = millis();
  if (now - arm.lastSwingTime < 400) return; // debounce

  float dTheta = endAngle - arm.startAngle;
  ++arm.swingCount;
  float arcLen = fabsf(dTheta) * arm.radius;
  arm.swingDistanceSum += arcLen;

  PRINT("Swing "); PRINT(arm.label);
  PRINT(" #"); PRINT(arm.swingCount);
  PRINT(" │ Angle: "); PRINT(fabsf(dTheta)*57.29578f);
  PRINT(" ° │ Length: "); PRINTLN(arcLen*100.0f);

  arm.lastSwingTime = now;
  arm.inSwing = false;
  arm.dir = 0;
}

/* ── Update swing ── */
void updateArm(Arm &arm, float dt) {
  sensors_event_t a, g, t;
  arm.mpu->getEvent(&a, &g, &t);
  float wy_raw = g.gyro.y;
  float wy = wy_raw - arm.bias;
  arm.angle += wy * dt;

  float aMag = sqrtf(a.acceleration.x*a.acceleration.x + a.acceleration.y*a.acceleration.y + a.acceleration.z*a.acceleration.z);
  bool accelTrigger = fabsf(aMag-9.8f) > ACCEL_MAG_THRESH_DELTA;

  if (!arm.inSwing) {
    if (accelTrigger) {
      if (wy > GYRO_THRESH_FWD) arm.inSwing = true, arm.dir=+1, arm.startAngle=arm.angle, arm.swingStartMs=millis();
      else if (wy < -GYRO_THRESH_BACK) arm.inSwing = true, arm.dir=-1, arm.startAngle=arm.angle, arm.swingStartMs=millis();
    }
  } else {
    bool crossed = (arm.dir==+1 && wy<-GYRO_THRESH_BACK)||(arm.dir==-1 && wy>GYRO_THRESH_FWD);
    uint32_t elapsed = millis() - arm.swingStartMs;
    bool zeroLike = (fabsf(wy)<WY_IDLE)&&(elapsed>END_ZERO_CROSS_MS);
    bool timeout = elapsed>SWING_MAX_MS;
    if(crossed||zeroLike||timeout) printSwing(arm, arm.angle);
  }

  if(fabsf(wy)<WY_IDLE) arm.bias = (1.0f-BIAS_ADAPT_ALPHA)*arm.bias + BIAS_ADAPT_ALPHA*wy_raw;
}

/* ── Send to Google Sheets ── */
void sendToGoogleSheets() {
  if (WiFi.status() != WL_CONNECTED) return;
  HTTPClient http;
  http.begin(scriptURL);
  http.addHeader("Content-Type","application/json");
  float left_cm = left.swingDistanceSum*100.0f;
  float right_cm = right.swingDistanceSum*100.0f;
  String json="{";
  json += "\"leftCount\":" + String(left.swingCount) + ",";
  json += "\"leftDistance\":" + String(left_cm,2) + ",";
  json += "\"rightCount\":" + String(right.swingCount) + ",";
  json += "\"rightDistance\":" + String(right_cm,2) + "}";
  PRINTLN("Sending JSON: "+json);
  int code = http.POST(json);
  PRINT("HTTP Response code: "); PRINTLN(code);
  http.end();
  left.swingCount=0; right.swingCount=0; left.swingDistanceSum=0; right.swingDistanceSum=0;
}

/* ── Feedback ── */
void feedback() {
  uint32_t lc=left.swingCount, rc=right.swingCount;
  float ld=left.swingDistanceSum, rd=right.swingDistanceSum;
  if((lc+rc)==0||(ld+rd)==0){ analogWrite(PIN_VIBE_LEFT,0); analogWrite(PIN_VIBE_RIGHT,0); return; }
  float countFracL=float(lc)/float(lc+rc);
  float distFracL=ld/(ld+rd);
  float leftShare=(countFracL+distFracL)/2.0f;
  const float DZ=0.055f;
  float delta=fabs(leftShare-0.5f);
  if(delta<=DZ){ analogWrite(PIN_VIBE_LEFT,0); analogWrite(PIN_VIBE_RIGHT,0); return; }
  float intensity=(delta-DZ)/(0.5f-DZ);
  if(intensity<0) intensity=0; ifanalogWrite(PIN_VIBE_LEFT,0); analogWrite(PIN_VIBE_RIGHT,pwm)(intensity>1) intensity=1;
  int   =int(255.0f*intensity);
  if(leftShare<0.3f){ analogWrite(PIN_VIBE_LEFT,pwm); analogWrite(PIN_VIBE_RIGHT,0); }
  else if(leftShare>0.3f && leftShare<0.7f){}
  else { analogWrite(PIN_VIBE_LEFT,0); analogWrite(PIN_VIBE_RIGHT,pwm); }
}

/* ── Priming phase with 90th percentile ── */
float calculatePercentile(std::vector<float> &data, float percentile){
  if(data.size()==0) return 0;
  std::sort(data.begin(),data.end());
  size_t idx=int(percentile*data.size());
  if(idx>=data.size()) idx=data.size()-1;
  return data[idx];
}

void primingPhase(Arm &arm, uint32_t durationMs){
  std::vector<float> posSamples, negSamples, accelSamples;
  uint32_t start=millis();
  analogWrite(PIN_VIBE_LEFT,255);
  analogWrite(PIN_VIBE_RIGHT,255);
  while(millis()-start<durationMs){
    sensors_event_t a,g,t;
    arm.mpu->getEvent(&a,&g,&t);
    float wy = g.gyro.y - arm.bias;
    float aMag = sqrtf(a.acceleration.x*a.acceleration.x + a.acceleration.y*a.acceleration.y + a.acceleration.z*a.acceleration.z);
    if(wy>0) posSamples.push_back(wy);
    else if(wy<0) negSamples.push_back(fabs(wy));
    accelSamples.push_back(aMag);
    delay(1000/SAMPLE_RATE_HZ);
  }
  analogWrite(PIN_VIBE_LEFT,0);
  analogWrite(PIN_VIBE_RIGHT,0);
  GYRO_THRESH_FWD = calculatePercentile(posSamples,0.9f);
  GYRO_THRESH_BACK = calculatePercentile(negSamples,0.9f);
  ACCEL_MAG_THRESH_DELTA = fmaxf(2.0f,fabs(calculatePercentile(accelSamples,0.9f)-9.8f));
}

/* ── Motor countdown ── */
void motorCountdown(int times,uint32_t onMs){
  for(int i=0;i<times;i++){
    analogWrite(PIN_VIBE_LEFT,255);
    analogWrite(PIN_VIBE_RIGHT,255);
    delay(onMs);
    analogWrite(PIN_VIBE_LEFT,0);
    analogWrite(PIN_VIBE_RIGHT,0);
    delay(500);
  }
}

/* ── Setup ── */
void setup() {
  if(Serial) Serial.begin(115200);
  Wire.setClock(100000);
  Wire.begin(SDA_PIN,SCL_PIN);

  WiFi.begin(ssid,password);
  while(WiFi.status()!=WL_CONNECTED){ delay(500); }

  if(!mpuRight.begin(ADDR_RIGHT)){ while(1) delay(10); }
  if(!mpuLeft.begin(ADDR_LEFT)){ while(1) delay(10); }

  mpuLeft.setGyroRange(MPU6050_RANGE_500_DEG);
  mpuRight.setGyroRange(MPU6050_RANGE_500_DEG);
  mpuLeft.setFilterBandwidth(MPU6050_BAND_21_HZ);
  mpuRight.setFilterBandwidth(MPU6050_BAND_21_HZ);

  calibrateGyro(left);
  calibrateGyro(right);

  pinMode(PIN_VIBE_LEFT,OUTPUT);
  pinMode(PIN_VIBE_RIGHT,OUTPUT);
  analogWrite(PIN_VIBE_LEFT,0);
  analogWrite(PIN_VIBE_RIGHT,0);

  lastMicros=micros();
  lastSendTime=millis();

  primingPhase(left,5000);
  primingPhase(right,5000);
  delay(5000);
  motorCountdown(3,3000);
}

/* ── Loop ── */
void loop() {
  uint64_t now=micros();
  float dt=(now-lastMicros)*1e-6f;
  lastMicros=now;

  updateArm(left,dt);
  updateArm(right,dt);

  if(millis()-lastSendTime>=10000){
    feedback();
    sendToGoogleSheets();
    lastSendTime=millis();
  }

  delayMicroseconds(1000000/SAMPLE_RATE_HZ-200);
}
